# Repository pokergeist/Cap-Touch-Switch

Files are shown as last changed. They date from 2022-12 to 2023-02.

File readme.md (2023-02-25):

# Cap Switch Project

## Introduction

This project aims to create a capacitive touch switch that uses a CR2032 button cell to power a capacitive touch sensor and solid state relay to to assist with switch-adapting a device for assistive technology purposes. The relay is rated at 2A continuous, 40V.

## Status

|    Date    | Status                                                       |
| :--------: | ------------------------------------------------------------ |
| 2023-02-25 | Revising for polarity issue & new JST PH connector. Rev 2b.  |
| 2023-01-12 | All done for now.                                            |
| 2023-01-06 | Boards received, testing underway.                           |
| 2022-12-29 | Boards ordered.                                              |
| 2022-12-27 | Driver circuit simulated. Bench testing and transistor selection pending. |
| 2022-12-23 | Working to support multiple battery options.                 |
| 2022-12-21 | First posting. Untested.                                     |

**2022-02-25**

The Eagle model for the coin cell was wrong and the polarity was backwards so that has been fixed. A JST PH-2 connector (B2.2) option was added. The XH-2 connector (B2.1) was moved into the coin cell (B1) area making them mutually exclusive. Rev 2b.

**2021-01-12**

The new coin cell battery holders arrived and fit perfectly. The current draw test results are [here](board/Current-and-Power-Draw.md).

**2023-01-06**

The boards have been received and (4) boards assembled. What's up:

* The Keystone #1026 button cell holder footprint is wrong (too big) due to their goofy datasheet but moded #103 should fit perfectly since that is what was depicted. Ordering those from Mouser.
* I quickly tested (4) boards with a Lithium pouch (LiPo) cell and the Cap Touch sensor is working fine . I'll be testing with other voltages and testing the SS Relay and capturing video too.
* I need more transistors and relays to populate many more boards, and some new coin cell holders.

**2022-12-27**

A current driver circuit has been selected. See board/[readme](#board/readme.md) file.

**2022-12-23**

I want to test some voltage regulation circuits to see so I can protect the SS Relay (<25mA) while reducing the current (and  power) draw toward the lower level and extending functionality over the range of whatever battery option is used.

## Todo

* Add on-off switch?
* Make sure SSR height (4mm) doesn't interfere with board mounting and sensor access.

## Mounting

The board is intended to be mounted with the cap sensor exposed. There are 3.5mm holes for securing with M3 screws or 3D printed posts.

On the bottom is a button cell holder for (2) CR2016 cells.

## Cap Touch Sensor

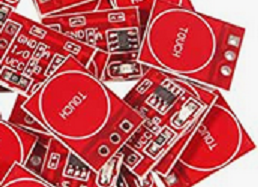
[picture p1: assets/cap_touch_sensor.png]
cap sensor


## Printed Circuit Board

Please refer to the board/[readme](board/readme.md) file for more info on the PCB.

### TTP223-BA6 Pinout & Modes

| Pin  | Function        |                                                              |
| :--: | --------------- | ------------------------------------------------------------ |
|  1   | Q               | Output pin (open drain).                                     |
|  2   | Vss (GND)       | Ground: 0V                                                   |
|  3   | I               | Input to Oscillator circuit.                                 |
|  4   | TOG (Jumper B)  | 1-Toggle or 0-Momentary mode.                                |
|  5   | Vdd (V+)        | Power: 2.0 - 5.5VDC                                          |
|  6   | AHLB (Jumper A) | Active 1-High or 0-Low output.                               |
|      | LPMB = 0        | Low Power Mode on. (Not Fast Mode)                           |
|      | MOTB = 1        | Max On Time 100s disabled. Infinite On if covered and detected. |
|      | SLRFTB = 1      | Sampling Rate: 1.6ms. Lower current and sensitivity.         |

### Board Jumpers

Leave Jumper A open for an Active High output unless you want to invert the operation of the relay.

Short Jumper B to switch from Momentary mode to Toggle mode.

## Run Time Calculations

| Item                                 | Capacity  / Current Draw | Hours  |
| ------------------------------------ | :----------------------: | :----: |
| Cell Capacity, CR2032                |    240mAh (at 200µA)     |        |
| Cap Touch Board                      |        3µA (max)         | 80,000 |
| Cap Touch Board & SS Relay (3V nom.) |          10.7mA          |  22.4  |

## Battery Options

Provisions for JST XH and PH headers have been added to facilitate the option of using an alternate battery pack. The 2.5mm pitch XH connectors handle bigger wire and are easier to crimp. The 2.0mm pitch PH connectors are common and can be plugged into Feather style microcontroller boards. Because the voltages vary different values for R1 may be necessary.

| Batteries Used                             | Max/Nom/Min Voltages |
| ------------------------------------------ | :------------------: |
| 1 x CR2032                                 |   3.4 / 3.0 / 2.7    |
| 2 x NiCd or NMH (recharable) AA or AAA     |   3.0 / 2.4 / 2.3    |
| 2 x Alkaline AA or AAA                     |    3.3 / 3.0 / ?     |
| 3 x NiCd or NMH (recharable) AA or AAA     |   4.5 / 3.6 / 3.45   |
| 3 x Alkaline AA or AAA                     |    4.95 / 4.5 / ?    |
| 1 x Li-ion (e.g. 18650) or LiPo pouch cell |   4.2 / 3.7 / 2.5    |
| 1 x LiFePO4 (LFP) cell                     |   3.65 / 3.2 / 2.0   |

**Do not use 2 x CR2016 cells** in the button cell holder as that exceeds the maximum voltage of the touch sensor.

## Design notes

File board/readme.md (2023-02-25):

# Cap Switch Board

## Introduction

This project aims to create a small capacitive touch switch that uses a CR2032 button cell to power a capacitive touch sensor and solid state relay to to assist with switch-adapting a device for assistive technology purposes. The relay is rated at 2A continuous, 40V.

Support for various battery options has been implemented via an external battery jack that can be connected to a battery or battery holder (AA, AAA, NiCd/NMH/Li-ion/LiPo/LiFePO4). Li-ion/LiPo charging via USB could be supported via the addition of a TP4056/DW01 module.

## Status

|    Date    | Status                                                      |
| :--------: | ----------------------------------------------------------- |
| 2023-02-25 | Revising for polarity issue & new JST PH connector. Rev 2b. |
| 2023-01-12 | All done for now.                                           |
| 2023-01-05 | Boards received and assembled. More parts ordered.          |
| 2022-12-29 | Boards ordered.                                             |
| 2022-12-27 | First posting. Untested.                                    |

**2022-02-25**

The Eagle model for the coin cell was wrong and the polarity was backwards so that has been fixed. A JST PH-2 connector (B2.2) option was added. The XH-2 connector (B2.1) was moved into the coin cell (B1) area making them mutually exclusive. Rev 2b.

**2021-01-12**

The new coin cell battery holders arrived and fit perfectly. Voltage and current test results are linked at the bottom.

**2023-01-06**

The boards have been received and (4) boards assembled. What's up:

* The Keystone #1026 button cell footprint is wrong (too big) due to their goofy datasheet, but moded #103 should fit perfectly since that is what was depicted. Ordering those from Mouser.
* I quickly tested (4) boards with a Lithium pouch (LiPo) cell and the Cap Touch sensor is working fine . I'll be testing with other voltages and testing the SS Relay and capturing video too.
* I need more transistors and relays to populate many more boards, and some new coin cell holders.

## Todo

* Add on-off switch?
* Make sure SSR height (4mm) doesn't interfere with board mounting and sensor access.

## Components

Two options are provided for powering this board. Parts for one option or the other could be purchased, or both.

1. a CR2032 "coin"cell
2. some combination of AA, AAA (alkaline or rechargeable NMH) or a Li-ion, Li-Po, or LiFePO4 lithium cell. (Do not exceed the 5.5V maximum voltage of the touch sensor.)

The first will use the coin cell holder, the second will use a JST XH 2.5mm or similar 2.54mm pitch connection option.

| Component                            | Source                                                       | Specs                                                        |
| ------------------------------------ | ------------------------------------------------------------ | ------------------------------------------------------------ |
| Capacitive touch sensor board (S1)   | [HiLetgo TTP223-BA6 Cap Switch](https://smile.amazon.com/dp/B01D1D0FLG) (Amazon ) ([datasheet](../assets/Cap-Touch-TTP223.pdf)) | 2.0-5.5V  3µA max Toggle\|Momentary, Active High\|Low        |
| Solid State Relay (K1)               | [Toshiba TLP241A,TP1](https://www.digikey.com/short/rw8vd8dn) ([datasheet](https://toshiba.semicon-storage.com/info/TLP241A_datasheet_en_20200217.pdf?did=14237&prodName=TLP241A)) | LED: 7.5mA Vf: 1.27V<br>Iout: 2A continuous, 6A pulsed<br>Ron: 90mΩ<br>40V |
| NPN Transistors Q1,Q2                | On Semi [PN2222ABU](https://www.digikey.com/short/n4rrtfnb)  | 40V 1A 625mW                                                 |
| Resistor 1.0 / 2.2 / 3.3kΩ (R1) 1206 | D-K [search](https://www.digikey.com/short/ff9cftjb)         | 1/4W 5% 1206                                                 |
| Resistor 47 - 56Ω (R2) 1206 (*)      | D-K [search](https://www.digikey.com/short/tv9vv7dh)         | 1/4W 5% 1206                                                 |
| Switch Lead Connector                | 0.1" or 2.54mm pitch connector or header posts               |                                                              |
| **Button Cell Option**               |                                                              |                                                              |
| Coin Cell Holder (B1)                | [Keystone #103](https://mou.sr/3W5l7RQ) ([datasheet](https://www.mouser.com/datasheet/2/215/03-745368.pdf)) | 4.5mm standoffs, (1) CR2032<br/> or (2) CR2016 or 2025s      |
| ~~Coin Cell Holder (B1)~~            | ~~[Keystone 1026](https://www.digikey.com/short/f35w9mv4) ([datasheet](https://www.keyelco.com/userAssets/file/M65p3.pdf))~~ | Doesn't fit                                                  |
| CR2032 Coin Cells (B1)               |                                                              | 3V nominal                                                   |
| **External Battery Option**          |                                                              |                                                              |
| External Battery Connector B2.1      | JST [XH header](https://www.digikey.com/short/9hf4mnvj) 2-position, 2.5mm pitch, straight |                                                              |
| External Battery Connector B2.2      | JST [PH header](https://www.digikey.com/short/wp55373q) 2-position, 2.0mm pitch, straight |                                                              |
| Battery Holder Pigtail Connector     | JST [XH housing](https://www.digikey.com/short/7fpfp333) 2-position, 2.5mm pitch |                                                              |
| Pigtail Connector Contacts (x 2)     | JST [XH contact](https://www.digikey.com/short/d91c10q9)     |                                                              |

\* Values need to be verified with test hardware (pending).

Using lower resistance values for R1 will increase the current draw ever so slightly.

Using lower resistance values for R2 will increase the current draw by a meaningful amount.

## Mounting

The board is intended to be mounted with the cap sensor exposed. There are 3.5mm holes for securing with M3 screws or 3D printed posts.

On the bottom is a button cell holder for (1) CR2032 cells.

## Cap Touch Sensor

cap sensor

## Printed Circuit Board

### Top

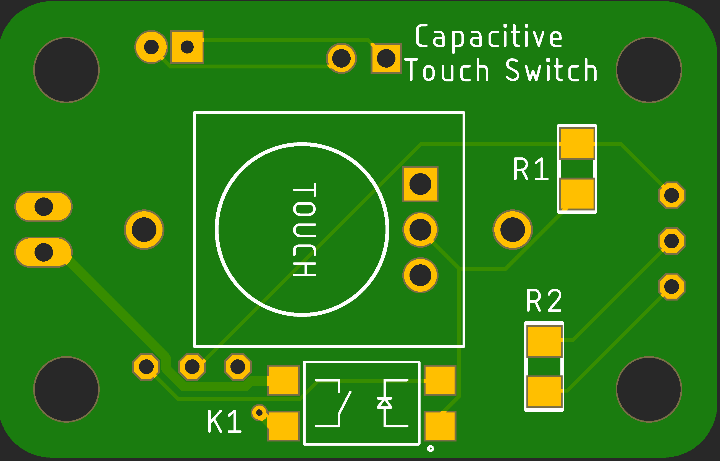
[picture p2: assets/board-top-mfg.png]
top


### Bottom

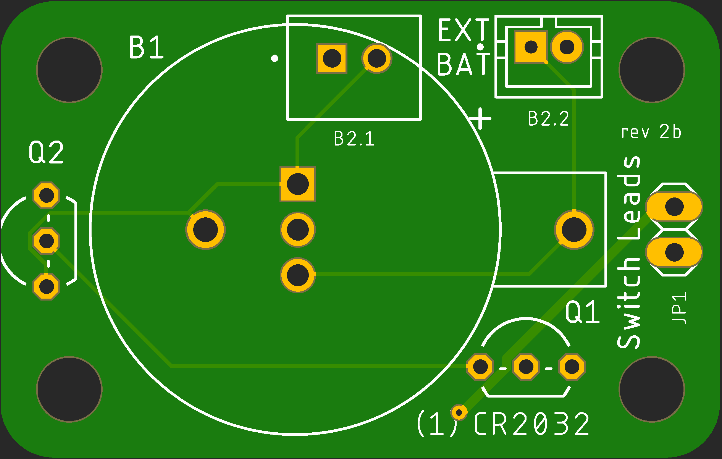
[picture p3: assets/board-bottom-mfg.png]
bottom


### Schematic

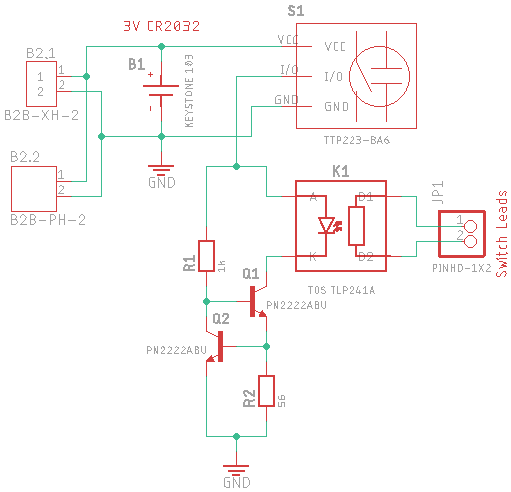
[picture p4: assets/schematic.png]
schematic


## TTP223-BA6 Pinout & Modes

| Pin  | Function        |                                                              |
| :--: | --------------- | ------------------------------------------------------------ |
|  1   | Q               | Output pin (open drain).                                     |
|  2   | Vss (GND)       | Ground: 0V                                                   |
|  3   | I               | Input to Oscillator circuit.                                 |
|  4   | TOG (Jumper B)  | 1-Toggle or 0-Momentary mode.                                |
|  5   | Vdd (V+)        | Power: 2.0 - 5.5VDC                                          |
|  6   | AHLB (Jumper A) | Active 1-High or 0-Low output.                               |
|      | LPMB = 0        | Low Power Mode on. (Not Fast Mode)                           |
|      | MOTB = 1        | Max On Time 100s disabled. Infinite On if covered and detected. |
|      | SLRFTB = 1      | Sampling Rate: 1.6ms. Lower current and sensitivity.         |

### Board Jumpers

Leave Jumper A open for an Active High output unless you want to invert the operation of the relay.

Short Jumper B to switch from Momentary mode to Toggle mode.

## Run Time Calculations

| Item                       | Capacity  / Current Draw | Hours  |
| -------------------------- | :----------------------: | :----: |
| Cell Capacity, CR2032      |    240mAh (at 200µA)     |        |
| Cap Touch Board            |        3µA (max)         | 80,000 |
| Cap Touch Board & SS Relay |          10.7mA          |  22.4  |

External battery options will provide considerably longer run times.

## Battery Options

A JST XH socket has been added to provide the option of using an alternate battery pack.

| Batteries Used                             | Max/Nom/Min Voltages (<5.5V!) |
| ------------------------------------------ | :---------------------------: |
| 1 x CR2032                                 |        3.4 / 3.0 / 2.7        |
| 2 x NiCd or NMH (recharable) AA or AAA     |        3.0 / 2.4 / 2.3        |
| 2 x Alkaline AA or AAA                     |         3.3 / 3.0 / ?         |
| 3 x NiCd or NMH (recharable) AA or AAA     |       4.5 / 3.6 / 3.45        |
| 3 x Alkaline AA or AAA                     |        4.95 / 4.5 / ?         |
| 1 x Li-ion (e.g. 18650) or LiPo pouch cell |        4.2 / 3.7 / 2.5        |
| 1 x LiFePO4 (LFP) cell                     |       3.65 / 3.2 / 2.0        |

**Do not use 2 x CR2016 cells** in the button cell holder as that exceeds the maximum voltage of the touch sensor.

## LED Current Driver

This 2-transistor current driver will maintain the SS Relay optical input current at about 10mA across the input voltage range of 2.0 to 4.5V. The circuit is simulated at [Falstad circuit.js](https://tinyurl.com/2kyk5f8h) with sliders on the right for input voltage and the collector resistor value. There's an ammeter and voltage probe for the LED.

The top transistor will conduct current until the voltage drop across the 56Ω resistor approaches 0.7V, turning on the lower transistor. As the lower transistor turns on it will start pulling the base of the upper transistor to ground, turning off the upper transistor which will reduce the LED current to an equilibrium point.

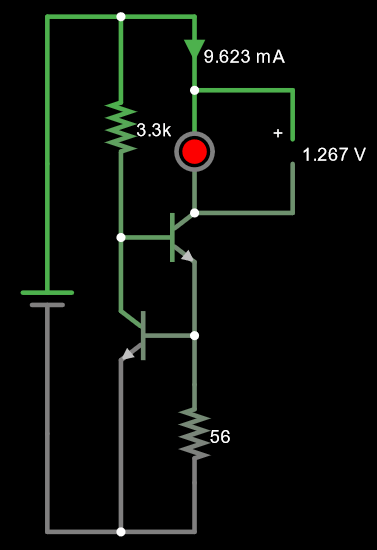
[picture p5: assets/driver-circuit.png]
LED driver circuit


## Voltage, Current, & Power Measurements

Measurements were taken using input voltages from 1.5 (the minimum) to 5.0V. The greatest efficiency is at low votage where the sensor's LED is barely on and the power lost at Q1 is minimal.

The measurement log is [here](Current-and-Power-Draw.md).

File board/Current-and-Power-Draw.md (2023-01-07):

# Current & Power Draw

I stepped through voltages measuring the current and calculating the power draw. This includes current drawn by  the red LED on the red Cap Touch Sensor board. The voltage settings were from an uncalibrated power supply and an uncalibrated but fairly new digital multimeter.

| **Volts** | **milliAmps** | **milliWatts** |
| :-------: | :-----------: | :------------: |
|    1.5    |     1.01      |      1.52      |
|    1.6    |     1.40      |      2.24      |
|    1.7    |     1.40      |      2.38      |
|    1.8    |     2.33      |      4.19      |
|    1.9    |     2.86      |      5.43      |
|    2.0    |     3.40      |      6.80      |
|    2.1    |     4.01      |      8.42      |
|    2.2    |     4.61      |      10.1      |
|    2.3    |     5.29      |      12.2      |
|    2.4    |     5.98      |      14.4      |
|    2.5    |     6.78      |      17.0      |
|    2.6    |     7.46      |      19.4      |
|    2.7    |     8.23      |      22.2      |
|    2.8    |     8.91      |      24.9      |
|    2.9    |     9.80      |      28.4      |
|    3.0    |     10.64     |      31.9      |
|    3.2    |     12.4      |      39.7      |
|    3.4    |     14.2      |      48.3      |
|    3.6    |     15.65     |      56.3      |
|    3.8    |     17.0      |      64.6      |
|    4.0    |     18.3      |      73.3      |
|    4.2    |     19.7      |      82.7      |
|    4.4    |     21.0      |      92.4      |
|    4.5    |     21.7      |      97.7      |
|    4.6    |     22.3      |      103       |
|    4.7    |     23.0      |      108       |
|    4.8    |     23.6      |      113       |
|    4.9    |     24.3      |      119       |
|    5.0    |     25.0      |      125       |

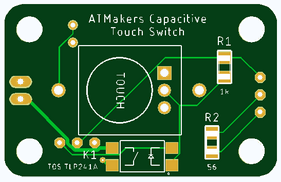
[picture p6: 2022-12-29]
assets/board-top-mfg-gerber.png

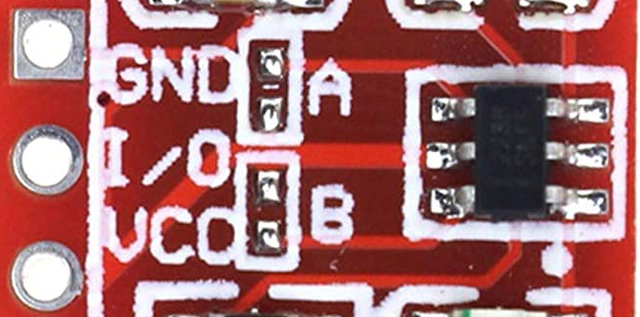
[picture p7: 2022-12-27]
assets/jumper-detail.png

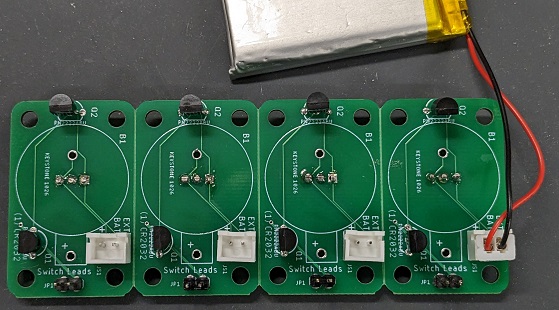
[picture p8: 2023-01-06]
assets/CapTouchSwitch_bottom.jpg

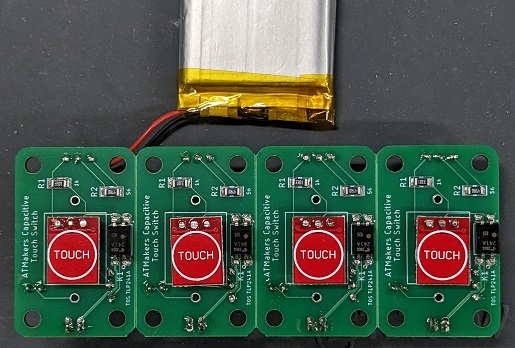
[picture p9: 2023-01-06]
assets/CapTouchSwitch_top.jpg

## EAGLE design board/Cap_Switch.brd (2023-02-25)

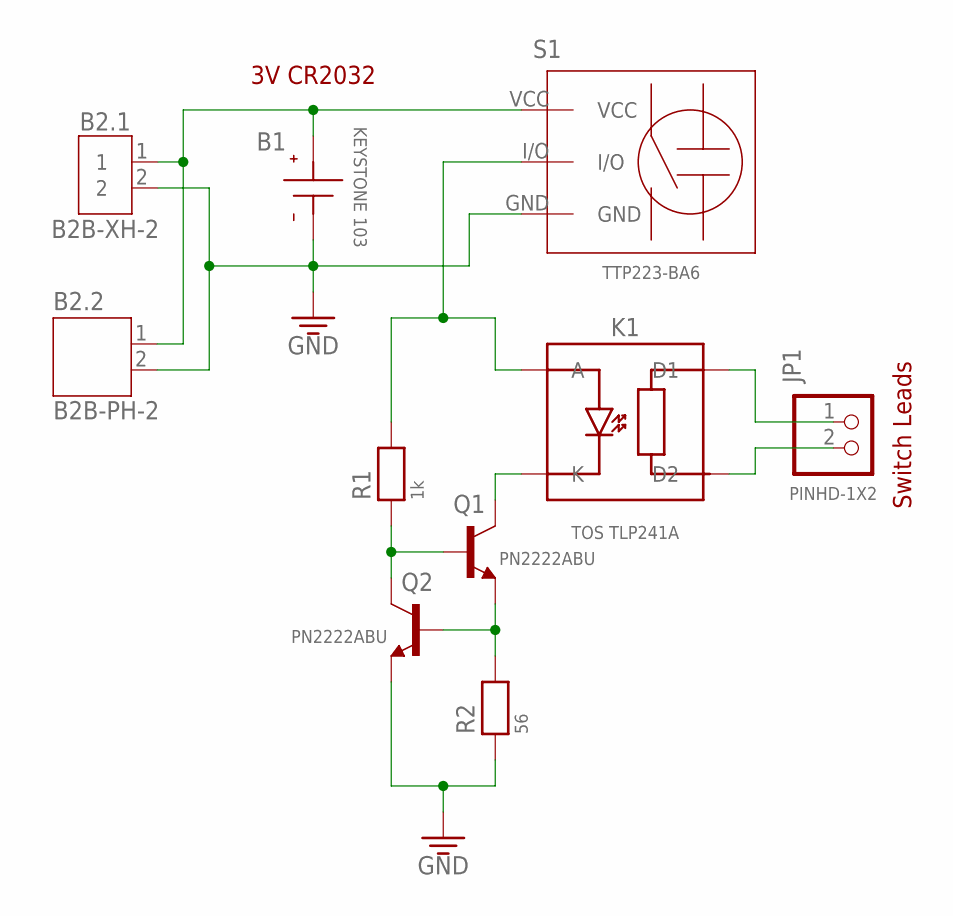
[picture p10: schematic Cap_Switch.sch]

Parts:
B1: KEYSTONE 103; 1026_KEY-103
B2.1: B2B-XH-2; B2B-XH-A
B2.2: B2B-PH-2; JST-PH2
JP1: PINHD-1X2; 1X02
K1: TOS TLP241A; TOS-TLP241A
Q1, Q2: PN2222ABU; TO92-
R1: 1k; 1206
R2: 56; 1206
S1: TTP223-BA6; SW-CAP-TOUCH-AMZN

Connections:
GND: B1.- (NEG), B2.1.2, B2.2.2, Q2.1 (E), R2.1, S1.GND
K: K1.P$2 (K), Q1.3 (C)
Q1-DRIVE: Q1.2 (B), Q2.3 (C), R1.1
Q2-DRIVE: Q1.1 (E), Q2.2 (B), R2.2
SW-A: JP1.1, K1.P$4 (D1)
SW-B: JP1.2, K1.P$3 (D2)
TRIGGER: K1.P$1 (A), R1.2, S1.I/O
V+: B1.+ (POS), B2.1.1, B2.2.1, S1.VCC

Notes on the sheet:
3V CR2032
Switch Leads

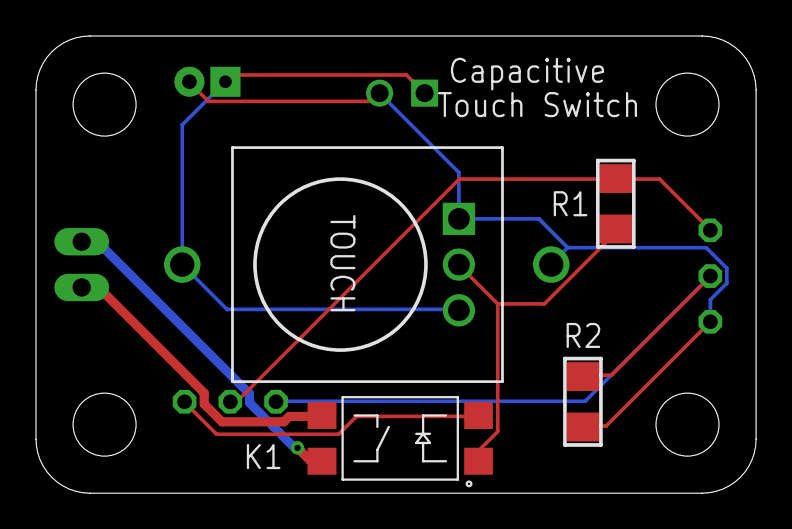
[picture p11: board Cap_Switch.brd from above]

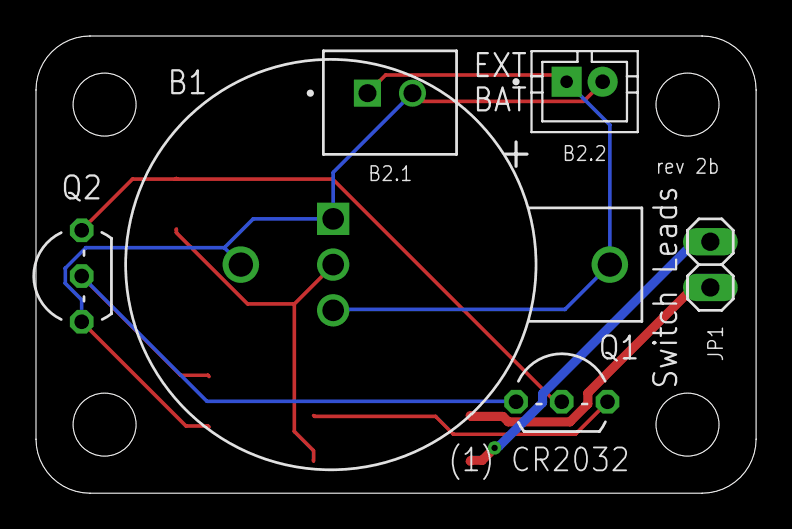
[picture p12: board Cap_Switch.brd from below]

Board: 2 copper layers, 40.0 x 25.4 mm, 10 parts (6 on the bottom side), 8 nets.

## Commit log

2022-12-22 ext battery options
2022-12-27 LED driver circuit
2022-12-27 board files
    [Cap_Switch.brd, Cap_Switch.sch]
2022-12-29 boards orderedd
    [Cap_Switch.brd]
2023-01-07 current measurements
2023-01-09 battery lead plug
2023-02-25 fixed coin cell polarity, new PH con
    [Cap_Switch.brd, Cap_Switch.sch]

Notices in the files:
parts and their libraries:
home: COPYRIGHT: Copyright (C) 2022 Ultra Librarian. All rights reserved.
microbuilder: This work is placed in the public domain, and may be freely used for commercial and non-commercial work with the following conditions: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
